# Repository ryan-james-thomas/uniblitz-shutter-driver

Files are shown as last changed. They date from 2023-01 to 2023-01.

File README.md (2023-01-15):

# Shutter Driver for uni-stable Uniblitz laser shutters

This shutter driver is designed to work with uni-stable Uniblitz shutters, and it is based on an old shutter driver design from the University of Otago Kjaergaard Lab.  It requires two power rails at +12 V and +60-70 V with a common ground.  When initially powered, up to two 47 uF capacitors are charged from the high-voltage rail, with the charging current being limited by up to four 1 kOhm, 2 W resistors.  On the rising edge of a control signal, this stored energy is switched into the shutter using two PNP transistors in the Darlington configuration which should give a nominal current spike of approximately 1.2 A.  The length of this spike can be varied by a factor of 2 using a trim-pot or, for shorter pulses, a capacitor (C3) can be replaced with a smaller value.  Testing has shown that a 1 nF capacitor and a total of 200 kOhm of resistance between R8 and RV1 will open shutters in good condition.  When the inital voltage/current spike has decayed a 200 mA holding current is provided to keep the shutter open.  To close the shutter the holding current is switched off using another PNP transistor.  To reduce voltage transients and ensure a fast closing time, a reverse-biased diode and a 1.8 kOhm resistor are connected to the shutter net, and these act to increase the rate at which the inductively generated negative voltage transient decays.  

The control signal is generated from an isolated 3 - 5 V digital input.  The relative polarity between the control signal and the input can be changed using a SPST switch.

Each board will draw up to 300 mA of current at +12 V and 60 mA of current at +60 V for each current-limiting resistor (R5, R14-R16).  Most applications will only need one current-limiting resistor and one storage capacitor.  More of these allow for faster charging, more charge storage, and therefore shorter delays between 'on' events.

Lists of parts can be found in the files 'Shutter_Driver.txt' and 'Auxiliary Parts.txt'.

Project files created with KiCAD 5.1.4.

## Enclosure
A diagram for the drilling out mounting holes for an enclosure containing 5 boards can be found in the file enclosure.pdf

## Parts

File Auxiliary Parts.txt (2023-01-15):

Name: Fuse
Digikey: 507-1243-ND
Quantity/Board: 1
Description: 500 mA slow-blow fuse in a 5x20 mm glass cartridge package.  If the high-voltage is stuck, should blow in 2 s.

Name: 2x1 connector male
Digikey: S1012EC-02-ND
Quantity/Board: 1
Description: 2x1 male header to mount on board so that LED can be mounted on a box chassis.

Name: 2x1 connector female
Digikey: 2057-RS1-02-G-ND
Quantity/Board: 1
Description: 2x1 female header to solder to LED wires and connect to male header

Name: 3x1 connector female
Digikey: S7036-ND
Quantity/Board: 1
Description: 3x1 female header to solder to switch wires and mate with male switch header

Name: SPDT switch
Digikey: EG2350-ND
Quantity/Board: 1
Description: SPDT switch for inverting logic polarity

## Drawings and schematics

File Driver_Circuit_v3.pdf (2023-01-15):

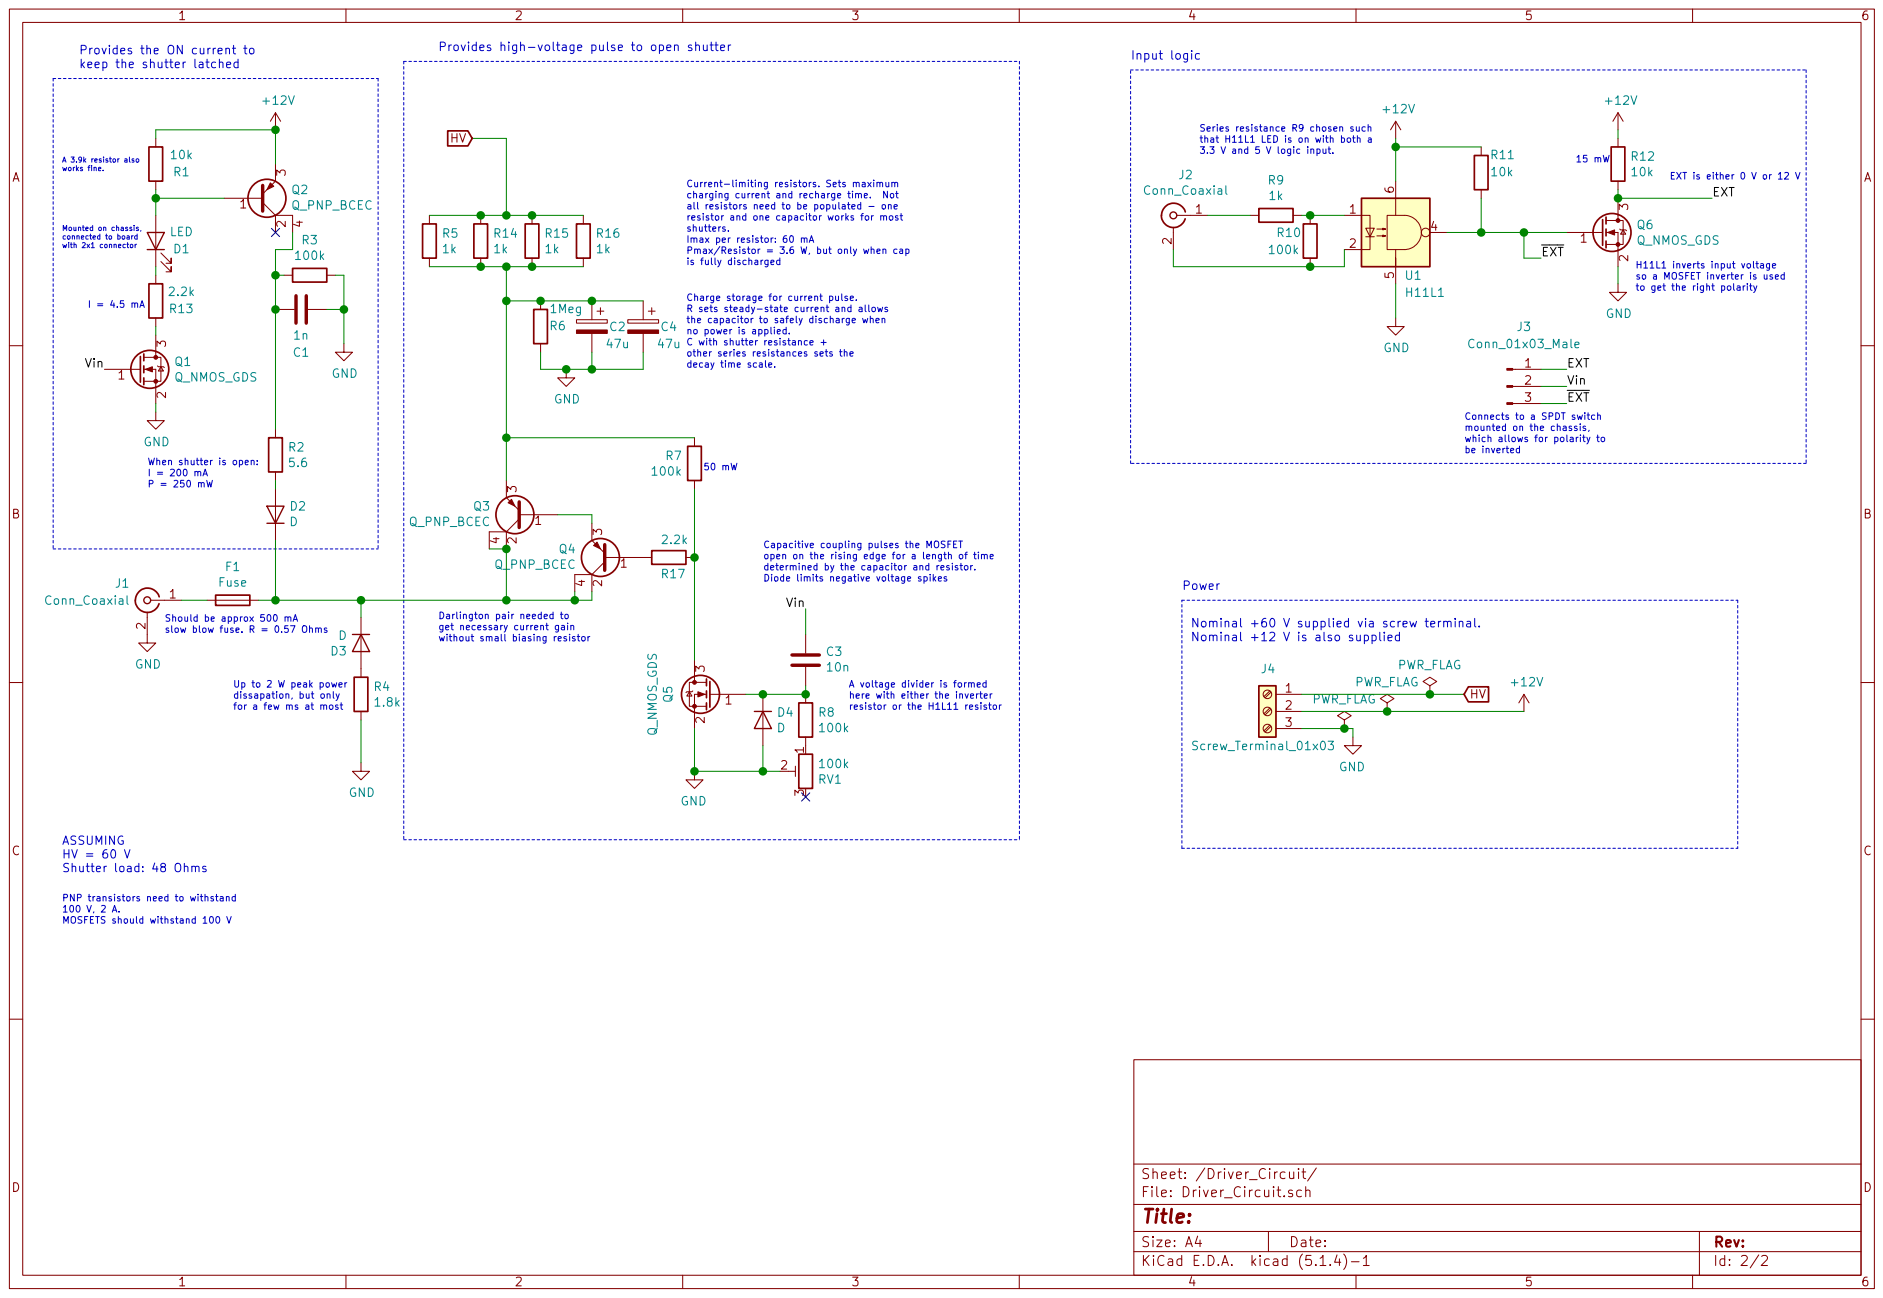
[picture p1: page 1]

keep the shutter latched ASSUMING
J2 Conn_Coaxial GND

that H11L1 LED is on with both a 3.3 V and 5 V logic input. Charge storage for current pulse. R sets steady-state current and allows

Series resistance R9 chosen such

determined by the capacitor and resistor. Diode limits negative voltage spikes Current-limiting resistors. Sets maximum
charging current and recharge time. Not all resistors need to be populated - one

Shutter load: 48 Ohms When shutter is open:

resistor and one capacitor works for most shutters.

Imax per resistor: 60 mA
Pmax/Resistor = 3.6 W, but only when cap

so a MOSFET inverter is used

to get the right polarity Should be approx 500 mA

the capacitor to safely discharge when
no power is applied. C with shutter resistance + other series resistances sets the

open on the rising edge for a length of time

Darlington pair needed to
get necessary current gain without small biasing resistor

Nominal +12 V is also supplied

here with either the inverter resistor or the H1L11 resistor PNP transistors need to withstand

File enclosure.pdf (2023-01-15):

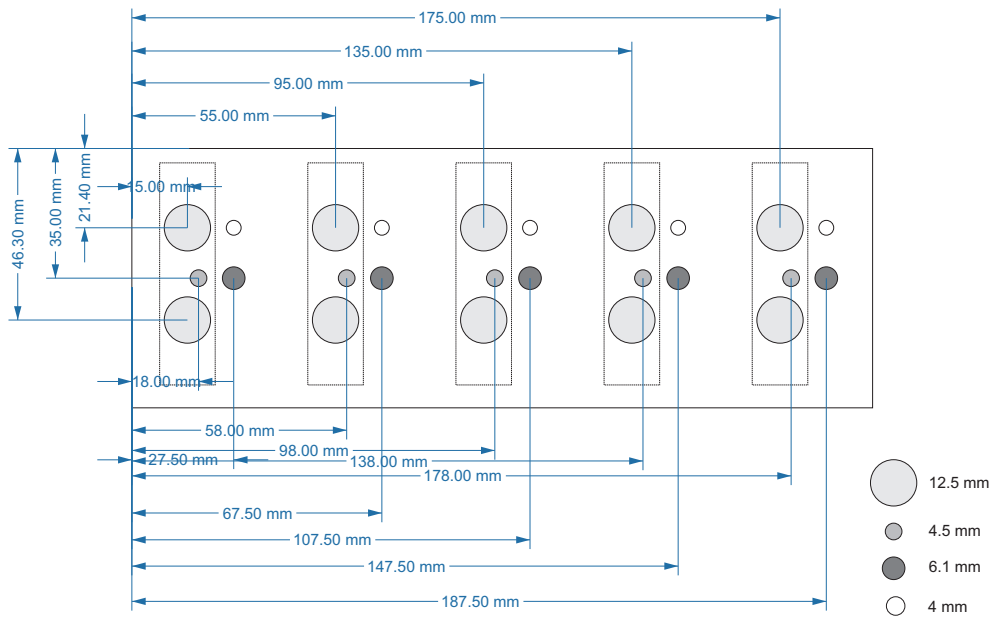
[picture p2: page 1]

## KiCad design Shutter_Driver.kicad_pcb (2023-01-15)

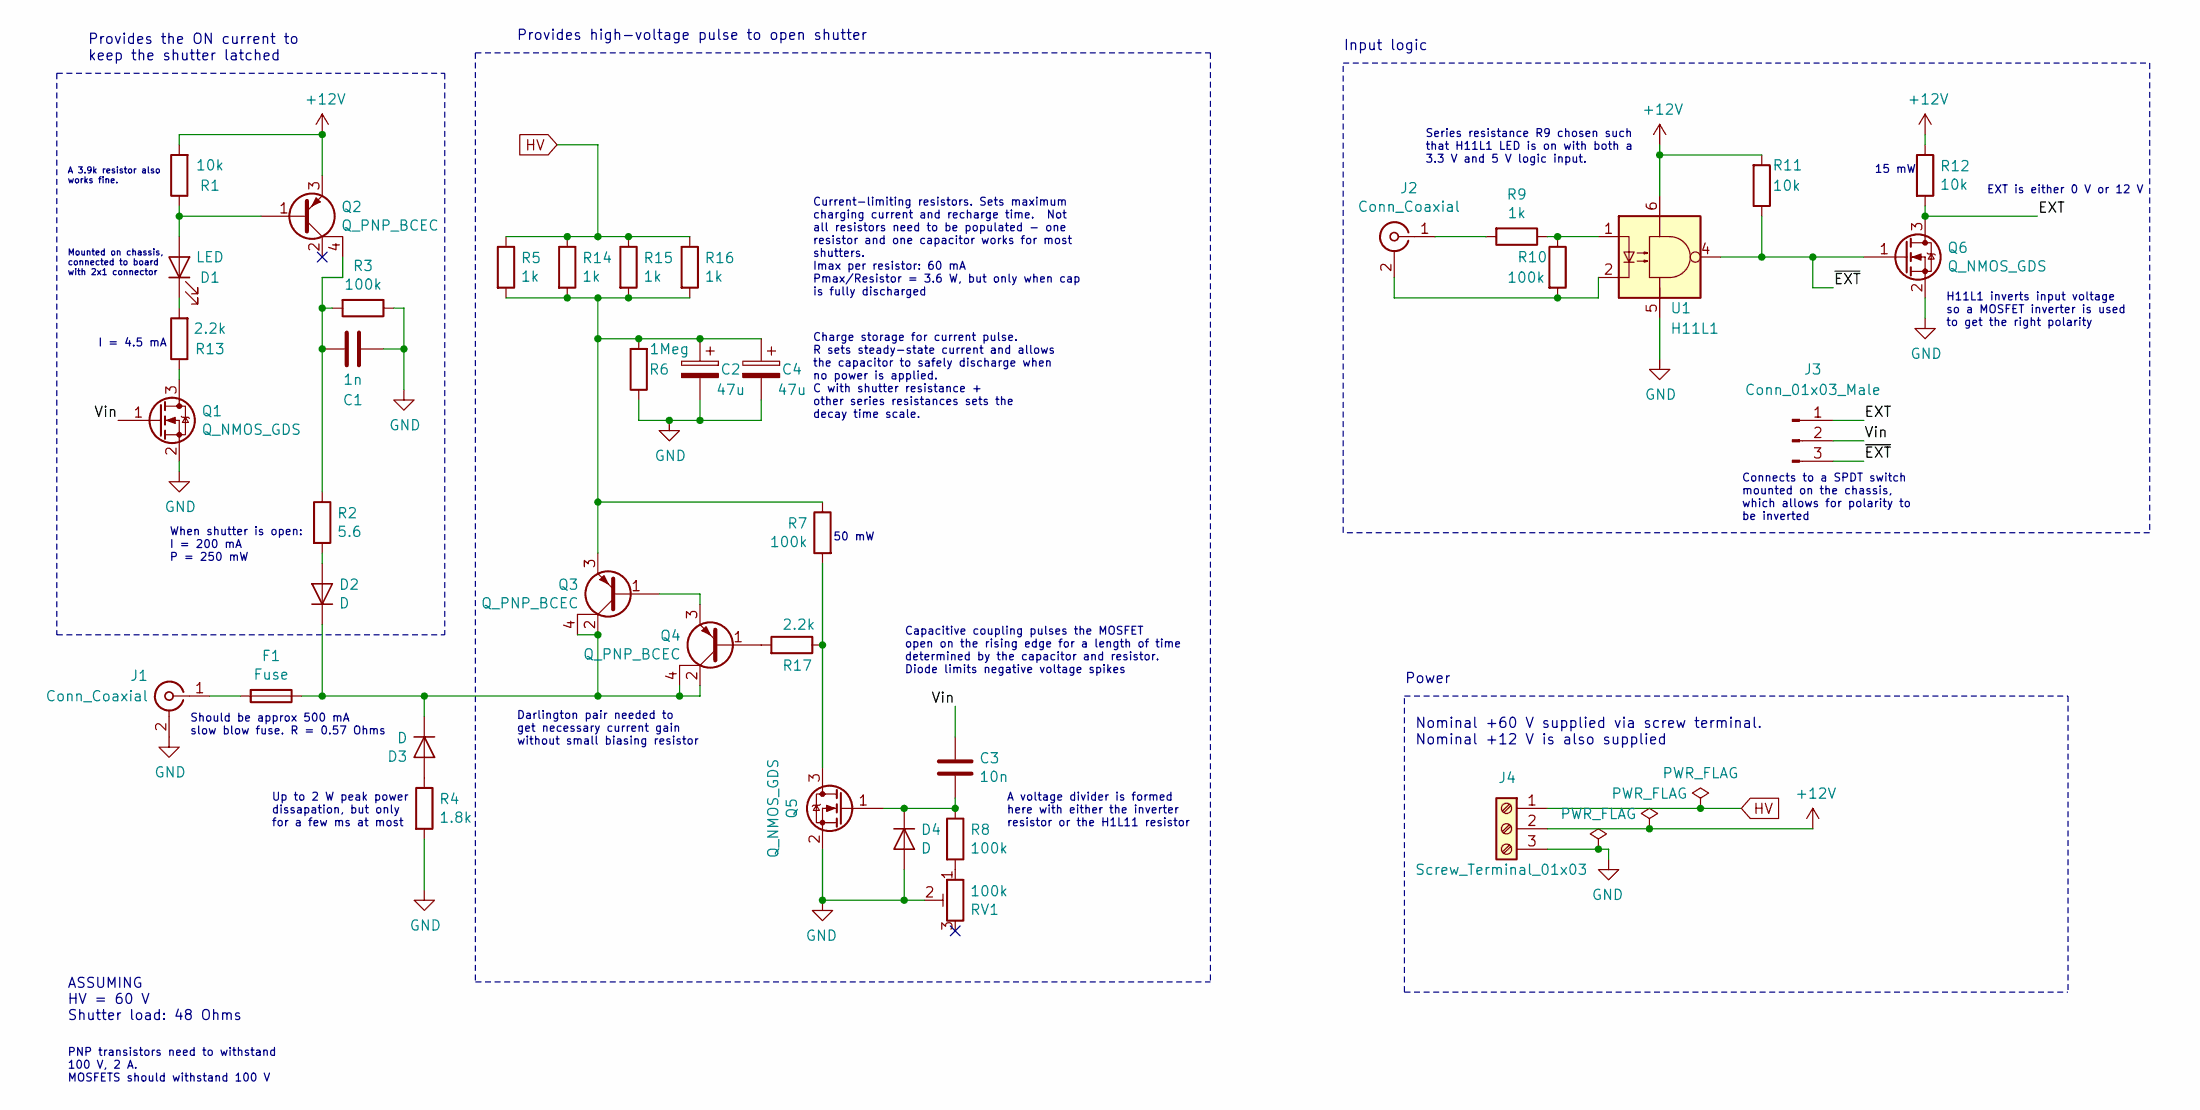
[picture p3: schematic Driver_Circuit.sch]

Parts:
C1: 1n; C_1206_3216Metric_Pad1.42x1.75mm_HandSolder; Digikey Part Number 732-8115-1-ND
C2, C4: 47u; CP_Radial_D10.0mm_P5.00mm; Digikey Part Number 399-15665-ND
C3: 10n; C_1206_3216Metric_Pad1.42x1.75mm_HandSolder; Digikey Part Number 1276-1035-1-ND
D1: LED; PinHeader_1x02_P2.54mm_Vertical; Digikey Part Number C5SMF-RJF-CT0W0BB1-ND
D2, D3, D4: D; D_5W_P10.16mm_Horizontal; Digikey Part Number 1N4005-TPMSCT-ND
F1: Fuse; Fuseholder_Wurth_15mm; Digikey Part Number 732-11374-ND
J1, J2: Conn_Coaxial; BNC_Amphenol_B6252HB-NPP3G-50_Horizontal; Digikey Part Number WM5514-ND
J3: Conn_01x03_Male; PinHeader_1x03_P2.54mm_Vertical; Digikey Part Number 2057-PH1-03-UA-ND
J4: Screw_Terminal_01x03; TerminalBlock_bornier-3_P5.08mm; Digikey Part Number 732-10956-ND
Q1, Q5, Q6: Q_NMOS_GDS; SOT-23_Handsoldering; Digikey Part Number BSS123-FDICT-ND
Q2, Q3, Q4: Q_PNP_BCEC; SOT-223; Digikey Part Number CZT955CT-ND
R1, R11, R12: 10k; R_1206_3216Metric_Pad1.42x1.75mm_HandSolder; Digikey Part Number RMCF1206JT10K0CT-ND
R2: 5.6; R_Axial_DIN0207_L6.3mm_D2.5mm_P10.16mm_Horizontal; Digikey Part Number S5.6HCT-ND
R3, R7, R8, R10: 100k; R_1206_3216Metric_Pad1.42x1.75mm_HandSolder; Digikey Part Number RMCF1206JT100KCT-ND
R4: 1.8k; R_Axial_DIN0207_L6.3mm_D2.5mm_P10.16mm_Horizontal; Digikey Part Number CF12JT1K80CT-ND
R5, R14, R15, R16: 1k; R_Axial_DIN0414_L11.9mm_D4.5mm_P15.24mm_Horizontal; Digikey Part Number RSMF2JT1K00CT-ND
R6: 1Meg; R_1206_3216Metric_Pad1.42x1.75mm_HandSolder; Digikey Part Number RMCF1206JG1M00CT-ND
R9: 1k; R_1206_3216Metric_Pad1.42x1.75mm_HandSolder; Digikey Part Number RMCF1206JT1K00CT-ND
R13, R17: 2.2k; R_1206_3216Metric_Pad1.42x1.75mm_HandSolder; Digikey Part Number RMCF1206JT2K20CT-ND
RV1: 100k; Potentiometer_Bourns_3296X_Horizontal; Digikey Part Number 490-2895-ND
U1: H11L1; SMDIP-6_W9.53mm; Digikey Part Number 1080-1201-1-ND

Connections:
+12V: J4.2, Q2.3 (E), R1.2, R11.2, R12.1, U1.6
/Driver_Circuit/EXT: J3.1, Q6.3 (D), R12.2
/Driver_Circuit/Vin: C3.2, J3.2, Q1.1 (G)
/Driver_Circuit/~EXT: J3.3, Q6.1 (G), R11.1, U1.4
GND: C1.2, C2.2, C4.2, D4.2 (A), J1.2 (Ext), J4.3, Q1.2 (S), Q5.2 (S), Q6.2 (S), R3.1, R4.2, R6.1, RV1.2, U1.5
HV: J4.1, R5.1, R14.1, R15.1, R16.1
unnamed: C1.1, Q2.4 (C), R2.1, R3.2
unnamed: C2.1, C4.1, Q3.3 (E), R5.2, R6.2, R7.1, R14.2, R15.2, R16.2
unnamed: C3.1, D4.1 (K), Q5.1 (G), R8.1
unnamed: D1.1 (K), R13.2
unnamed: D1.2 (A), Q2.1 (B), R1.1
unnamed: D2.1 (K), D3.1 (K), F1.1, Q3.2 (C), Q3.4 (C), Q4.2 (C), Q4.4 (C)
unnamed: D2.2 (A), R2.2
unnamed: D3.2 (A), R4.1
unnamed: F1.2, J1.1 (In)
unnamed: J2.1 (In), R9.2
unnamed: J2.2 (Ext), R10.2, U1.2
unnamed: Q1.3 (D), R13.1
unnamed: Q3.1 (B), Q4.3 (E)
unnamed: Q4.1 (B), R17.2
unnamed: Q5.3 (D), R7.2, R17.1
unnamed: R8.2, RV1.1
unnamed: R9.1, R10.1, U1.1

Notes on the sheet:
Series resistance R9 chosen such that H11L1 LED is on with both a 3.3 V and 5 V logic input.
H11L1 inverts input voltage so a MOSFET inverter is used to get the right polarity
Provides the ON current to keep the shutter latched
EXT is either 0 V or 12 V
Charge storage for current pulse. R sets steady-state current and allows the capacitor to safely discharge when no power is applied. C with shutter resistance + other series resistances sets the decay time scale.
When shutter is open: I = 200 mA P = 250 mW
ASSUMING HV = 60 V Shutter load: 48 Ohms
Darlington pair needed to get necessary current gain without small biasing resistor
50 mW
15 mW
Provides high-voltage pulse to open shutter
PNP transistors need to withstand 100 V, 2 A. MOSFETS should withstand 100 V
Connects to a SPDT switch mounted on the chassis, which allows for polarity to be inverted
Current-limiting resistors. Sets maximum charging current and recharge time. Not all resistors need to be populated - one resistor and one capacitor works for most shutters. Imax per resistor: 60 mA Pmax/Resistor = 3.6 W, but only when cap is fully discharged
Capacitive coupling pulses the MOSFET open on the rising edge for a length of time determined by the capacitor and resistor. Diode limits negative voltage spikes
A voltage divider is formed here with either the inverter resistor or the H1L11 resistor
Up to 2 W peak power dissapation, but only for a few ms at most
Nominal +60 V supplied via screw terminal. Nominal +12 V is also supplied
Power
Input logic
Mounted on chassis, connected to board with 2x1 connector
Should be approx 500 mA slow blow fuse. R = 0.57 Ohms
I = 4.5 mA
A 3.9k resistor also works fine.

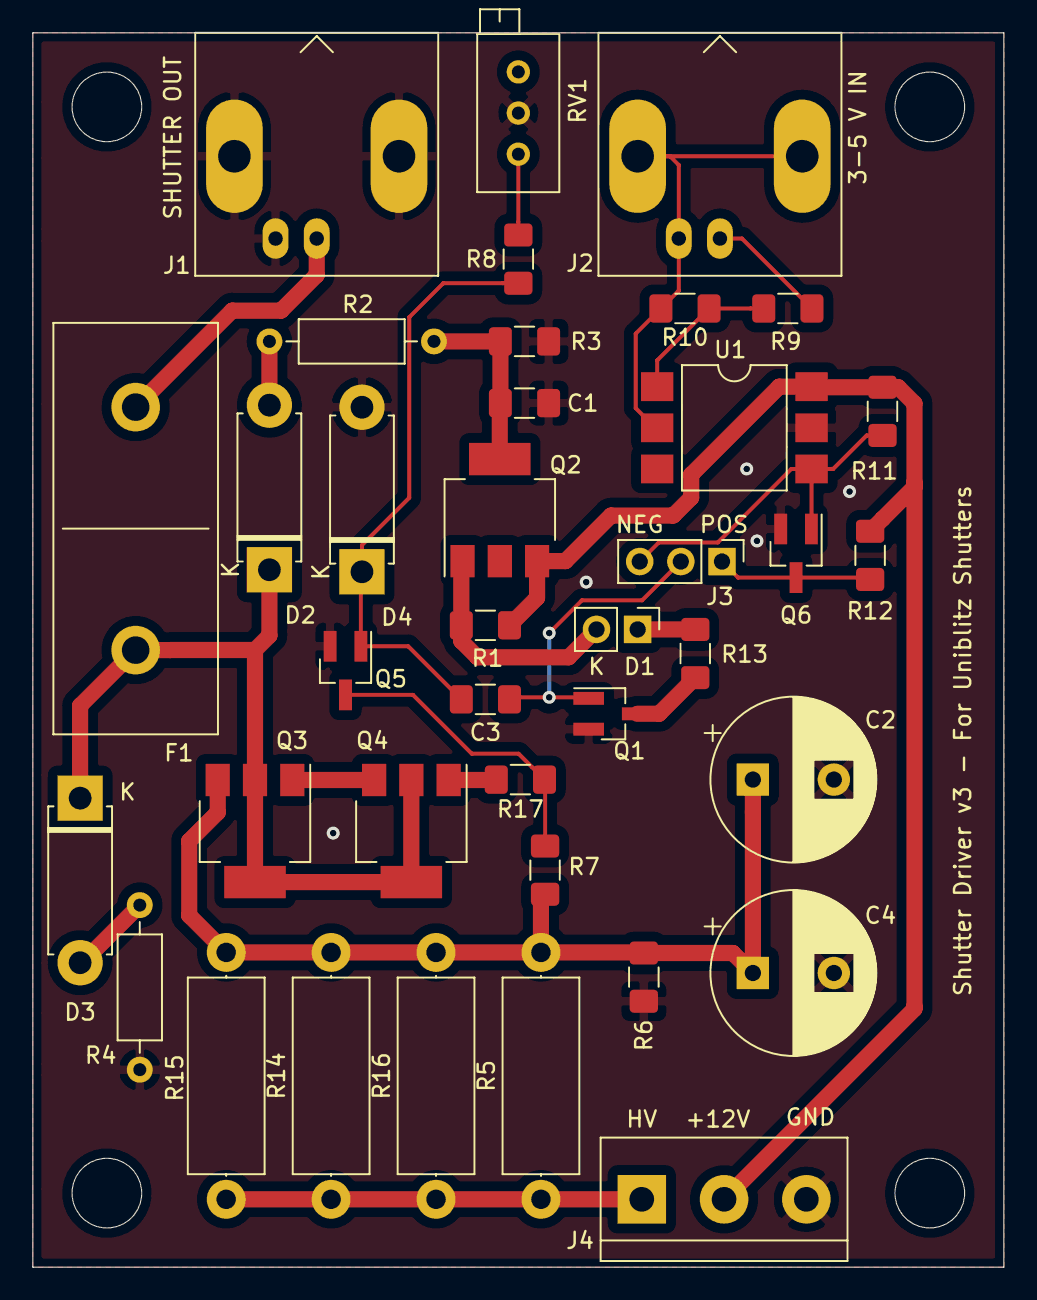
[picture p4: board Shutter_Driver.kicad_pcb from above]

Board: 2 copper layers, 59.9 x 76.2 mm, 38 parts (0 on the bottom side), 23 nets.
